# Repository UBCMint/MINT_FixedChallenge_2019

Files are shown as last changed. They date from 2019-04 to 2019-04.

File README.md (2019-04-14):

# Mentha 1.1

## Background

For the NeurotechX Fixed Challenge, MINT is building an EEG collection system from scratch, that will accurately and effectively collect scalp potentials and minimise noise.
The system will use an Arudino microcontroller to send the data aqcuired to the computer. We will then use a python script to live-plot the fourier transform of the data received. 

The UBC MINT EEG acquisition system consists of the following components:
- Differential amplifiers,
- Active analog low-pass filters,
- Analog to digital conversion,
- Digital 60 Hz notch filtering, and
- Display of the acquired EEG signals

The block diagram in Figure 1 shows the system as a whole.
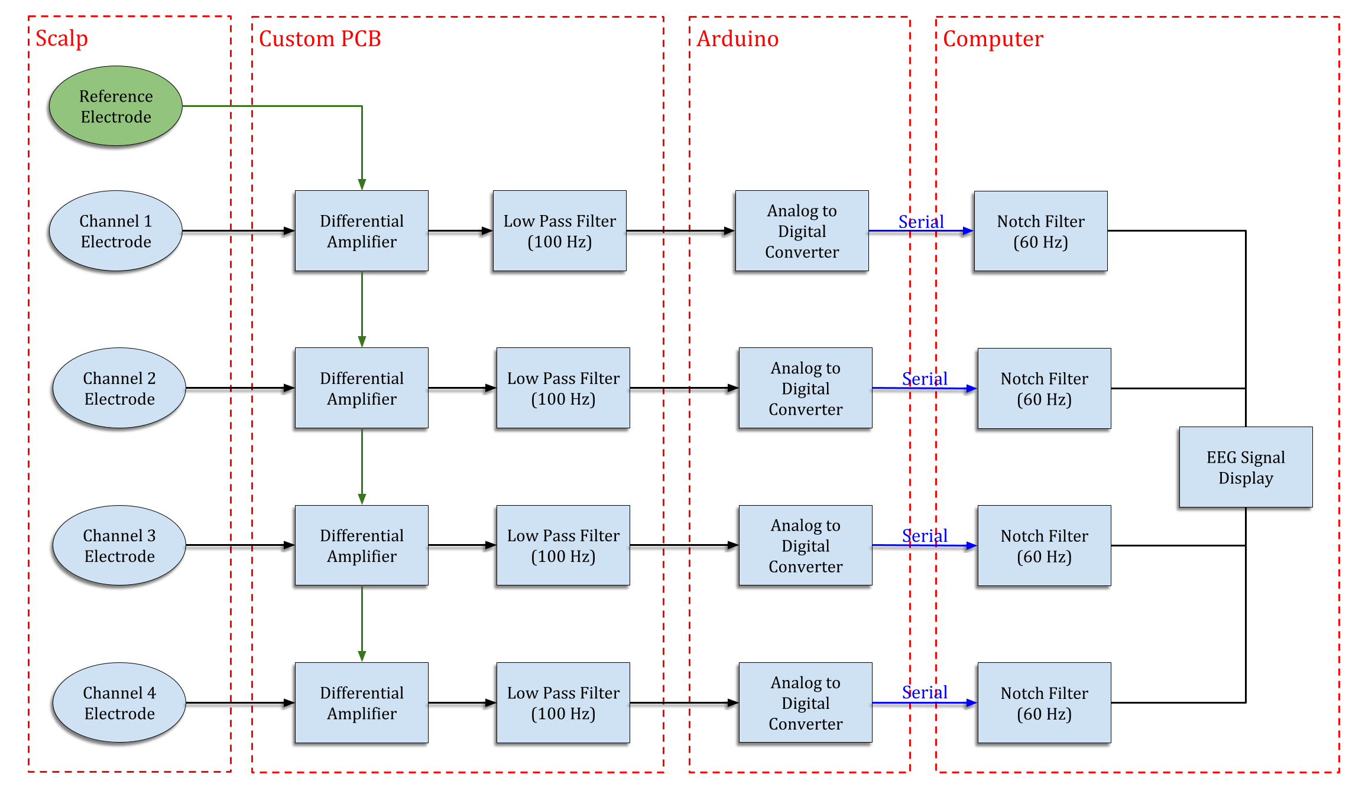
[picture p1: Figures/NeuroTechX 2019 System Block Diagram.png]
block diagram


Figure 1. System block diagram

We made our design choices based on availability and affordabiliity such that other teams can recreate our system. 

## Usage
This four channel EEG collection system can be easily set up and used. The scripts can be downloaded from the github repository and can be run with any Python interpreter. The four electrodes should be clipped onto the hair and placed closely against the scalp. Alternatively, gel electrodes can be placed on the forehead. 
The four electrode signals will be processed through the circuit and received by the Arduino Leo pins A0-A3. The 4 signals will be fourier transformed and displayed on the computer through a python plotting script. 

**Important**: Remember to change the port name to what you see in your Arduino IDE (e.g. "Arduino Leonardo on COM4") and to run the correct Arduino program for whichever script you're using (2Reads for 2Time2FFT.py, 4Reads for 4FFT.py)

## Electrodes
The chosen electrodes are gel electrodes, chosen for their ease of accessibility and use.

## Differential Amplifier
The chosen differential amplifier used in each channel is the AD620 instrumental amplifier. The AD620 is chosen for its low cost and high accuracy. Furthermore, it has low noise, low input bias current, and low power consumption characteristics.

The circuit schematic for the differential amplifier is shown in Figure 2 below.
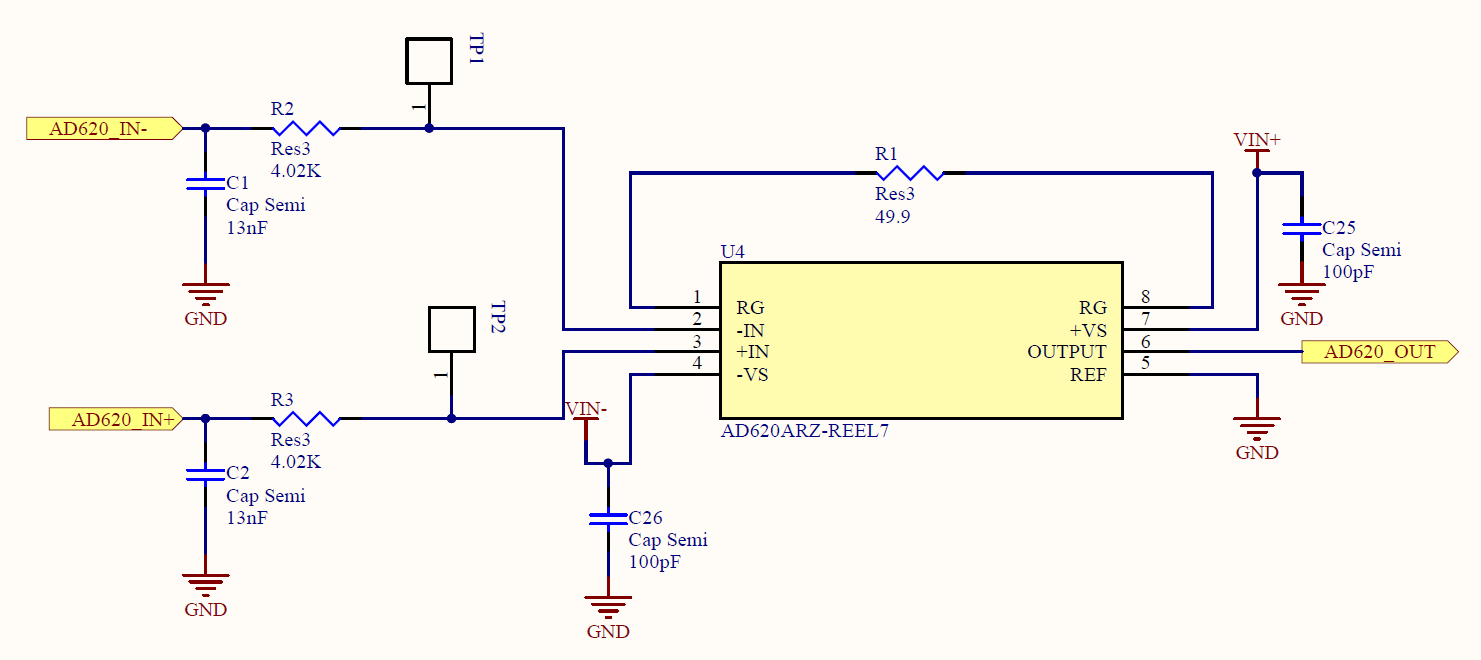
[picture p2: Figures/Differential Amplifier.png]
Differential Amplifier


Figure 2. Differential amplifier circuit schematic

The positive input (AD620_IN+) is from an electrode placed on the scalp. The negative input (AD620_IN-) is from an electrode placed on a bony body part to use as a reference signal.
 
The AD620 gain is given by the following equation.

Gain equation

The AD620 is configured to have a gain of approximately 1000 by setting the single external gain resistor to 49Ω.  From this, the output signal of the AD620 (AD620_OUT) is a 1000x amplified version of the differential signal between the channel and the reference signal.

## Low Pass Filter
The low pass filter is an active, second-order Butterworth filter that attenuates frequencies above 100 Hz since the frequency range of EEG signals has a maximum of 100 Hz. The schematic of the Butterworth filter is shown in Figure 3. The OP281 is the dual operational amplifier that was chosen for the filter.

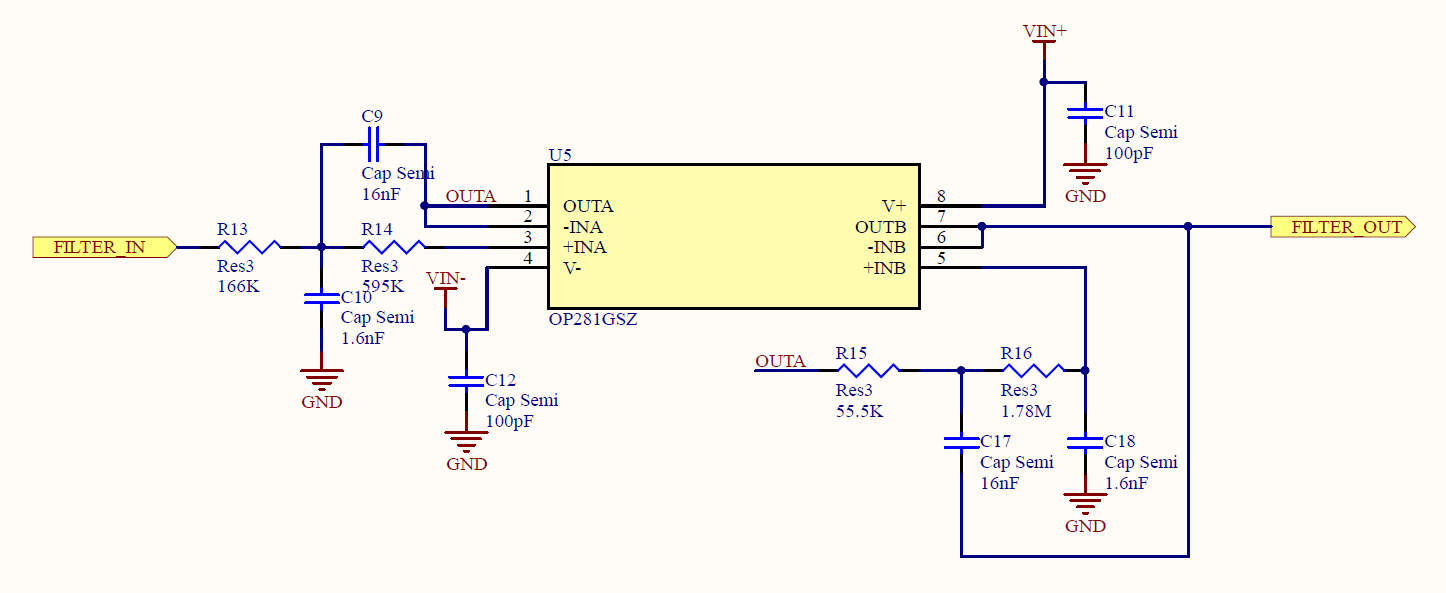
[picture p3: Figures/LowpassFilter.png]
Low pass Filter


Figure 3. Butterworth low pass filter amplifier circuit schematic

The analog outputs of the differential amplifiers are filtered before being converted to digital signals.

## PCB

We decided to use PCB instead of breadboard in order to reduce noise from the breadboard and the dangling wires. After determining the EEG circuit, we designed the PCB using Altium software and then put the electronic components on using solder paste stenciling and reflow oven.



Figure 4. Assemblied PCB with 4 channels.

## Analog to Digital Conversion
An Arduino Leonardo in conjunction with a Mayhew Labs extended ADC shield was chosen to perform analog to digital conversion on the amplified and filtered EEG signals. The extended ADC shield has 8 single-ended ADC inputs that can be sampled at 100 000 samples/s at a 16-bit resolution. It also allows for an input voltage range of -25 V to +25 V, enabling the direct use of the filtered EEG signal without requiring rectification.

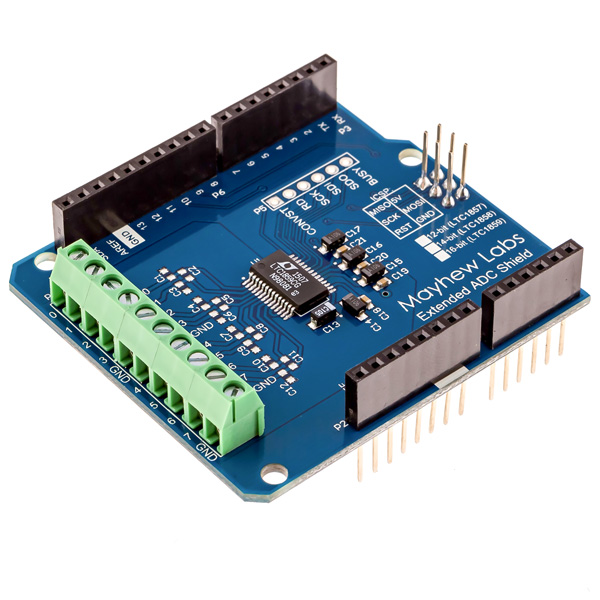
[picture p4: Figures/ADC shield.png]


Figure 5. Mayhew Labs extended ADC shield

## Digital Notch Filter & EEG Signal Display
The digital notch filter was done using Python in conjunction with the Num.py and PyQtGraph libraries to assist with the signal processing  and signal display. The filter takes the input and converts it into a 2D array which is then run through a FFT algorithm. Then, using a simple loop to remove all entries between index 59 and 61 (a particularly noisy frequency range) via the enumerate function, we were able to create the effect of a notch filter. The signal was then plotted using the PyQt graphing functions. To calibrate the graphing function to match with real time input we have to scale the index down by a factor of 2.13 and so the actual filter index we used was a range of 27-30hz.  

## Budget
- PCB $20
- Extended ADC Shield $48
- PCB Components $170
- Arduino Leonardo $40

Total = $278

## About Us

Mentha was created by the [(Multifaceted Innovation in NeuroTechnology](https://ubcmint.github.io/) (MINT) team of undergraduate students, part of the group [Biomedical Engineering Student Team](http://www.ubcbest.com/) at the University of British Columbia in Vancouver, Canada.

Mentha was submitted as a project for the Fixed Challenge category of the [NeuroTechX 2019 Student Club competition](https://neurotechx.github.io/studentclubs/competition/).
